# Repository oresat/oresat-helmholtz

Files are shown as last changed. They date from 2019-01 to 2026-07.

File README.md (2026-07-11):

# OreSat Helmholtz Cage



This repo contains design and operating instructions of a Helmholtz Cage, which uses the [Biot Savart Law](https://en.wikipedia.org/wiki/Biot%E2%80%93Savart_law) to get a desired magnetic field inside of an enclosed space using three pairs of perpendicular coils, one pair for each axis. Our fundamental purpose in doing this is to test cubesats' pointing and detumbling capabilities in LEO.

v2.0 is now underway, utilizing less hardware than v1.0. This is excellent news for everyone involved, as less parts means less things that can and will break. We are using a Raspberry Pi Pico to run it, with each set of coils getting their own motor driver, to drive the current, and a INA226 to monitor the current. A full schematic can be found [here](./controller-v2/helmholtz-controller-v2.kicad_sch). A PCB layout is in the works.

# Design Notes

**Status, design, and testing information can be found in the [OreSat Helmholtz Cage Design Notes](https://docs.google.com/document/d/1s9UlxD-V_3-_QfmXqKaY5oYsfC2GDHxeAkWD0VgjS5g/edit?tab=t.0).**

A seperate doc on the structure and design of the cage itself can be found [here](./docs/Open%20Source%20Document.docx). This doc is a bit out of date in some aspects, mainly the technical hardware, but serves as a good resource for cage construction and theory.

## Pictures
MCECS BETA Project 2018:


Current Build:
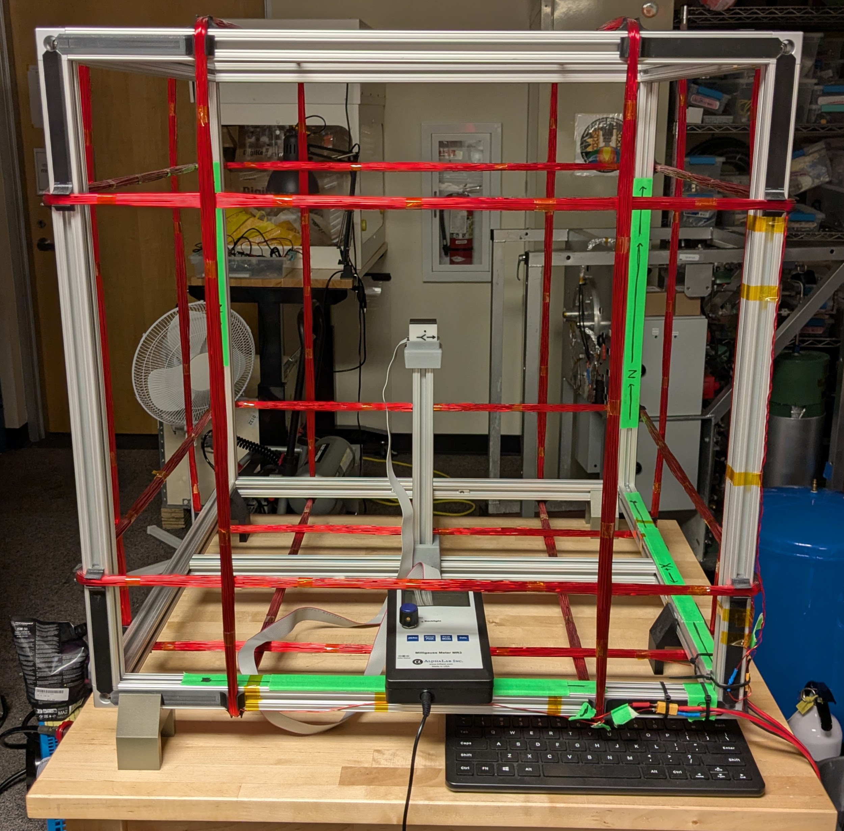
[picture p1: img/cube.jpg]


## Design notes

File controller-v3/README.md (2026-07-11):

---
title: "**Helmholtz Cage Controller v3.0**"
subtitle: |
  **Fabrication and Assembly Information**\
  For build TIME-STAMP
fontsize: 10pt
geometry:
  - margin=0.5in
toc: true
toc-depth: 2
colorlinks: true
urlcolor: blue
---

\newpage

# About this Board

## Board Description

This board controls the magnetic field in a small box with 3 double electromagnetic coils. 

TODO: MOAR

## Documentation Links

- Helmholtz Cage Controller v3: <https://github.com/oresat/oresat-helmholtz>

## Documentation Files

| Filename                        | Notes                                    |
| ------------------------------- | ---------------------------------------- |
| README.pdf                      | This README file                         |
| PROJECT-NAME-outline.dxf        | Board outline (with holes) in DXF format |
| PROJECT-NAME-pcba.step          | 3D model of PCBA (with components)       |
| PROJECT-NAME-render-bot.jpg     | Render of the top of the 3D model        |
| PROJECT-NAME-render-bot.jpg     | Render of the bottom of the 3D model     |
| PROJECT-NAME-schematic.pdf      | PDF of board schematics                  |

## Contact Information

- Website: <https://www.oresat.org/>
- Email: <oresat@pdx.edu>
- Instagram: @pdxaerospace

## Board Renders

Render of the top of the 3D model
Render of the bottom of the 3D model

\newpage

# Printed Circuit Board (PCB) Fabrication Information

## Board Info

- 2 layer board
- Bounding box is TBD
- Board thickness is 1.59 mm (0.063 inch)

## Board Requirements

- Design Rules
    - Minimum Trace / Space design rulea: 0.1524 mm (6.0 mil) / 0.1524 mm (6.0 mil)
    - Outer dimension router tolerance: +/- 0.254 mm (10.0 mil)
    - Hole placement tolerance: +/- 0.075 mm (3.0 mil)
- Drills
   - Drill Positional Tolerance: 0.051 mm (2.0 mil)
   - Drill Size tolerance: +/- 0.064 mm (2.5 mil)
- Plated/Un-plated holes
  - There are no un-plated (NPT) holes
  - There are 96 plated through (PTH) holes
  - PTH minimum diameter: 0.254 mm (10 mil)
  - PTH minimum annulus: 0.102 mm (4 mil) radius
- Outline/Routing
  - No requirements.
- Slots
  - There are no slots.
- Cutouts
  - There are no cutouts
- There are 3 fiducials on the top layer.
- Panel tabs ("mouse bites")
   - Card edges must be smooth; no mouse bites or other intrusions into the card outline.
   - If external mouse bites are required, minimize and customer will remove by hand before assembly.
- If not otherwise specified, build to IPC 6012 Class 2 or better.

## Materials

- No requirements for materials.
- Copper Surface treatment should be ENIG, althogh immersion Silver is acceptable.
- White silkscreen on top and bottom surface
- Taiyo PSR-4000 or equivalent soldermask on top and bottom, no requirements for color.

## Stack Up

- Any FR4 like material is acceptable.
- 1 oz Copper on top and bottom layers
- 1.6 mm thick when done (1/16 inch)

## Array / Panel Information

- Coordinate with Contract Manufacturer (CM) for optimal size of this panel.
- If no feedback from CM, then produce single boards (no panel).

## Fabrication Files

### IPC-2581 File

| Filename                 | Notes                                   |
| ------------------------ | --------------------------------------- |
| PROJECT-NAME-ipc2581.xml | IPC-2581 board information file         |

### Legacy PCB Files

| Filename                      | Notes                                         |
| ------------------------------| --------------------------------------------- |
| PROJECT-NAME-Edge_Cuts.gbr    | RS274X file for the dimension (outline) layer |
| PROJECT-NAME-F_Silkscreen.gbr | RS274X file for the top silkscreen            |
| PROJECT-NAME-F_Mask.gbr       | RS274X file for the top soldermask            |
| PROJECT-NAME-F_Cu.gbr         | RS274X file for the top copper layer          |
| PROJECT-NAME-In1_Cu.gbr       | RS274X file for the layer 2 copper            |
| PROJECT-NAME-In2_Cu.gbr       | RS274X file for the layer 3 copper            |
| PROJECT-NAME-B_Cu.gbr         | RS274X file for the bottom copper layer       |
| PROJECT-NAME-B_Mask.gbr       | RS274X file for the bottom soldermask         |
| PROJECT-NAME-B_Silkscreen.gbr | RS274X file for the bottom silkscreen         |
| PROJECT-NAME-NPTH.drl         | Excellon file for non-plated through holes    |
| PROJECT-NAME-PTH.drl          | Excellon file for plated through holes        | 

\newpage

# Printed Circuit Board Assembly (PCBA) Information

## Assembly Info

- All components are on the top side of the board.

## Assembly Requirements

- Assemble to IPC Class 2 or better
- Solder paste can be ROHS or leaded.
- No clean, or Aqueous flux and wash, can be used.
- No conformal coating.

## Component Specific Assembly Information

- None

## Assembly Files

### IPC-2581 File

| Filename                 | Notes                           |
| ------------------------ | ------------------------------- |
| PROJECT-NAME-ipc2581.xml | IPC-2581 board information file |

### Bill of Materials (BOM)

| Filename             | Description                            |
| -------------------- | -------------------------------------- |
| PROJECT-NAME-bom.csv | BOM in Comma Separated Variable format |

### Solder Paste Stencils

| Filename                 | Notes                                            |
| ------------------------ | ------------------------------------------------ |
| PROJECT-NAME-B_Paste.gbr | RS274X file for top/front solder paste stencil   |
| PROJECT-NAME-F_Paste.gbr | RS274X file for bottom/back solder paste stencil |

### Mounting/Placement Location

| Filename            | Description                                 |
| ------------------- | ------------------------------------------- |
| PROJECT-NAME-3u.pos | Pick and place locations for components     |

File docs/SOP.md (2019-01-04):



# OreSat Helmholtz Cage: Standard Operating Procedure

## General Notes:

* Operate the cage with 4.92 max amps and 15.20 max volts to output the largest magnetic field vector.
* Theoretical magnetic field vector equation:

  * Bz is the total field produced by both square coils as a function of the axial distance z from the center of the coils
  * u0 is the permeability of free space: 4pi*10^-7 WB A^-1 m^-1
  * n is the number of turns of wire: 58 turns
  * I is the current of the wire being analyzed: user input
  * h is the distance between the coils: 
  * a is one half the side length of the structure: 
  
**Do not operate the Helmholtz Cage if the vacuum chamber is on!**

---
## Safety:

* The red coils will get hot if operated for an extended period of time at high currents. Do not touch or hold the coils when operating the cage.
* Monitor the temperature of the wires to maintain a safe operating temperature below 140°C.
* Monitor the temperature of the main power supply to operate between -25°C to 70°C.
* If the temperature begins to approach the operating limits, turn off the power supply and let the cage cool down before resuming testing.

**Do not operate the Helmholtz Cage if the vacuum chamber is on!**

---
## Prepping the Cage:

1. It is safe to put electronic devices inside and around the cage. However, they may disrupt the magnetic field and cause discrepancies in testing data. Be mindful of this and be aware of the testing space surroundings.
2. Verify that the vacuum chamber is NOT on.
3. Verify that the coils are secured in the terminal blocks and make sure they are connected to the correct terminals/power supply. No exposed or crossing wires!
4. Turn on the surge protector. This will power the raspberry pi, monitor, power supplies, and cage.
5. Let the raspberry pi boot up.
6. Turn the keyboard and the mouse on. There are spare batteries in the tote just in case.

---
## Operating the Cage Program:

TBD

---
## Testing & Analyzing Data:

TBD

---
## While the Helmholtz Cage is Running:

* Do not leave the cage unattended. You must monitor it constantly in case of a fire, to maintain safe temperatures for components, and to ensure accurate data collection.
* When the cage is running, do not touch or hold the red coils! They get hot and can cause injury/burns.
* Turn off the surge protector to turn the cage of for any reason.

---
## Finishing Up:

1. Once testing is completed, turn off the raspberry pi using the desktop menu.
2. Wait for the raspberry pi to shutdown completely.
3. Turn off the keyboard and mouse!! Don’t waste the batteries!
4. Flip off the surge protector to power down the power supplies, monitor, and cage.
5. If you adjusted the coil placement, wait until the red wire is cool to the touch before returning the coils to their originally labelled terminals.
6. Clean up after yourself and keep the workstation organized!

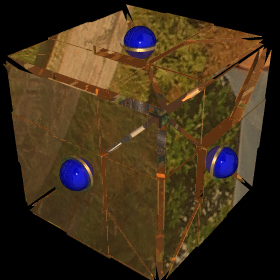
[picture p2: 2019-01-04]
img/holtz.jpg

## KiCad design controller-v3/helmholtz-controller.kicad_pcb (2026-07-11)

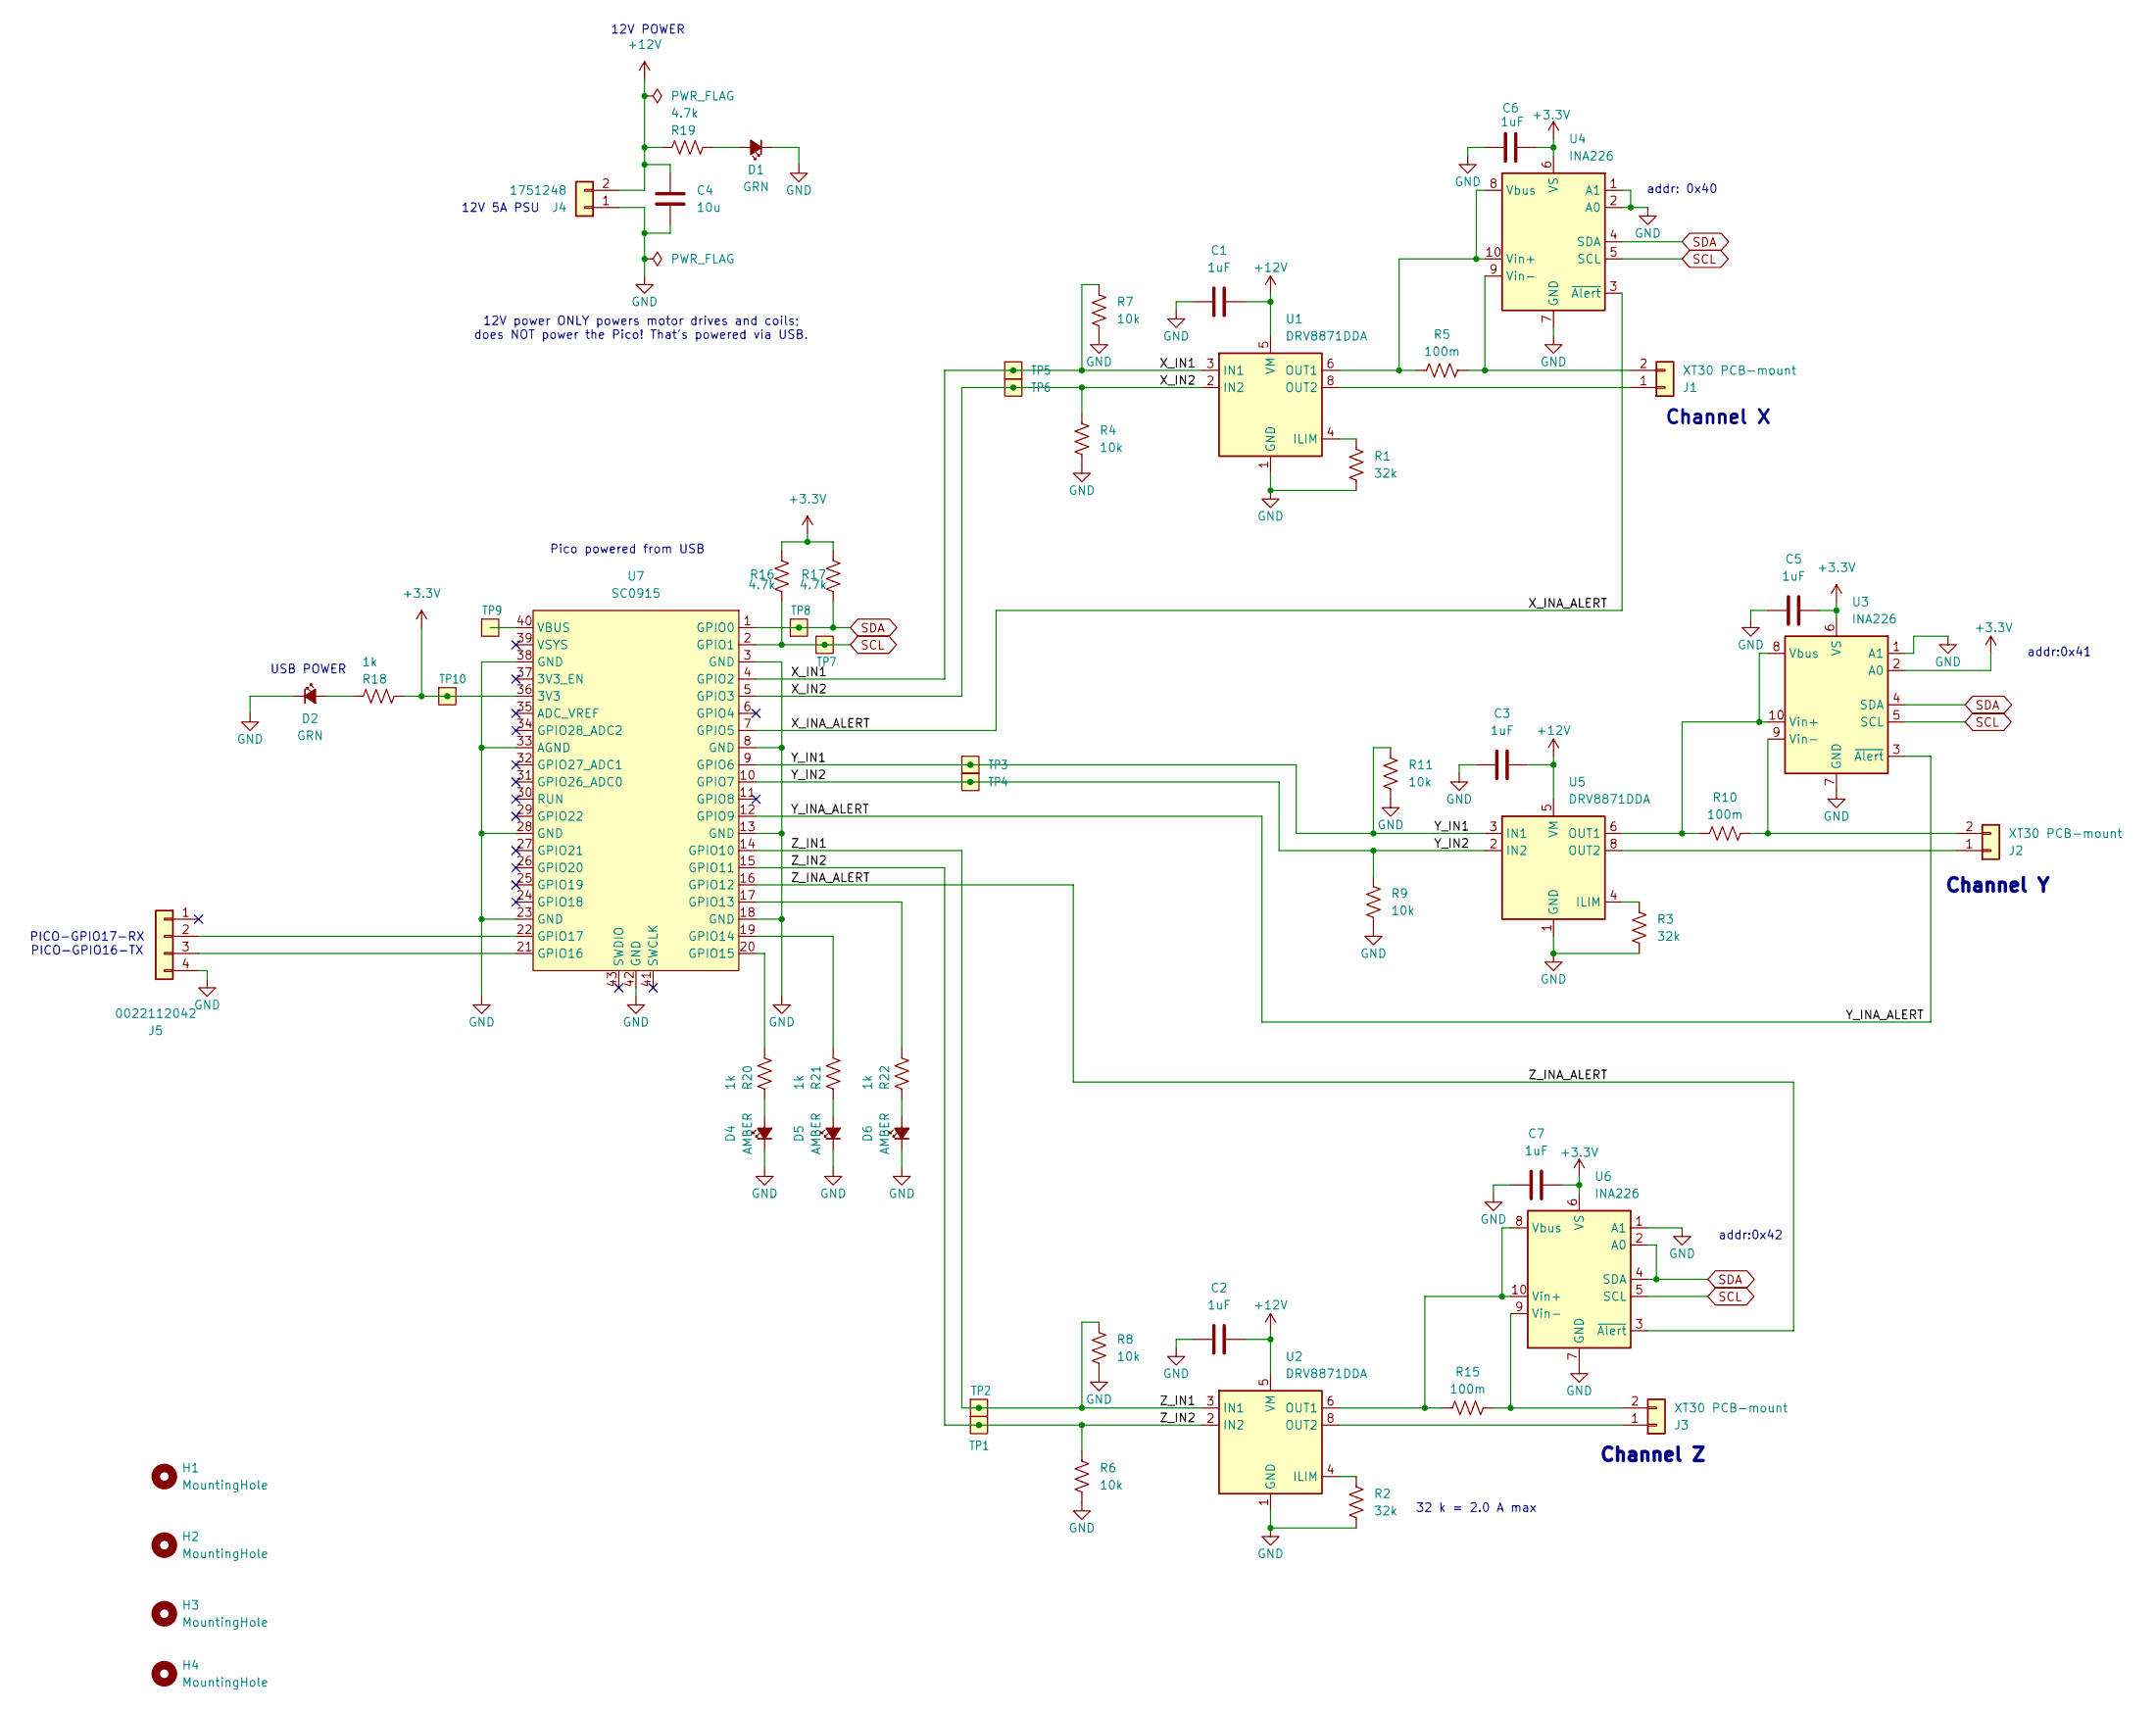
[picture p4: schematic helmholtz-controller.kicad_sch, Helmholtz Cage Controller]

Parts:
C1, C2, C3, C5, C6, C7: 1uF; C_0805_2012Metric; MPN GCM21BR71H105KA03L
C4: 10u; C_0805_2012Metric; MPN GRT21BC71E106KE13K
D1, D2: GRN; LED_0603_1608Metric; MPN 150060GS75000
D4, D5, D6: AMBER; LED_0603_1608Metric; MPN 150060AS75000
H1, H2, H3, H4: MountingHole; MountingHole_3.2mm_M3
J1, J2, J3: XT30 PCB-mount; AMASS_XT30PW-F_1x02_P2.50mm_Horizontal
J4: 1751248; TerminalBlock_Phoenix_PT-1,5-2-3.5-H_1x02_P3.50mm_Horizontal; MPN 1751248
J5: 0022112042; PinHeader_1x04_P2.54mm_Vertical; MPN 0022112042
R1, R2, R3: 32k; R_0603_1608Metric; MPN RNCF0603BTE32K0
R4, R6, R7, R8, R9, R11: 10k; R_0603_1608Metric; MPN RMCF0603FT10K0
R5, R10, R15: 100m; R_1206_3216Metric; MPN CSR1206FTR100
R16, R17, R19: 4.7k; R_0603_1608Metric; MPN RC0603FR-074K7L
R18, R20, R21, R22: 1k; R_0603_1608Metric; MPN RMCF0603FT1K00
TP1, TP2, TP3, TP4, TP5, TP6, TP7, TP8, TP9, TP10: Test-Point; TestPoint-0.75mm-th
U1, U2, U5: DRV8871DDA; Texas_HTSOP-8-1EP_3.9x4.9mm_P1.27mm_EP2.95x4.9mm_Mask2.4x3.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; MPN DRV8871DDA
U3, U4, U6: INA226; TSSOP-10_3x3mm_P0.5mm; MPN INA226AIDGST
U7: SC0915; RPi_Pico_Castellated; MPN SC0915

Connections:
+3.3V: C5.2, C6.2, C7.2, R16.2, R17.2, R18.2, TP10.1 (1_1), U3.2 (A0), U3.6 (VS), U4.6 (VS), U6.6 (VS), U7.36 (3V3)
+12V: C1.2, C2.2, C3.2, C4.2, J4.2, R19.1, U1.5 (VM), U2.5 (VM), U5.5 (VM)
/X_IN1: R7.1, TP5.1 (1_1), U1.3 (IN1), U7.4 (GPIO2)
/X_IN2: R4.1, TP6.1 (1_1), U1.2 (IN2), U7.5 (GPIO3)
/X_INA_ALERT: U4.3 (~Alert), U7.7 (GPIO5)
/Y_IN1: R11.1, TP3.1 (1_1), U5.3 (IN1), U7.9 (GPIO6)
/Y_IN2: R9.1, TP4.1 (1_1), U5.2 (IN2), U7.10 (GPIO7)
/Y_INA_ALERT: U3.3 (~Alert), U7.12 (GPIO9)
/Z_IN1: R8.1, TP2.1 (1_1), U2.3 (IN1), U7.14 (GPIO10)
/Z_IN2: R6.1, TP1.1 (1_1), U2.2 (IN2), U7.15 (GPIO11)
/Z_INA_ALERT: U6.3 (~Alert), U7.16 (GPIO12)
GND: C1.1, C2.1, C3.1, C4.1, C5.1, C6.1, C7.1, D1.1 (K), D2.1 (K), D4.1 (K), D5.1 (K), D6.1 (K), J4.1, J5.4, R1.2, R2.2, R3.2, R4.2, R6.2, R7.2, R8.2, R9.2, R11.2, U1.1 (GND), U1.7 (GND), U1.9 (GND), U2.1 (GND), U2.7 (GND), U2.9 (GND), U3.1 (A1), U3.7 (GND), U4.1 (A1), U4.2 (A0), U4.7 (GND), U5.1 (GND), U5.7 (GND), U5.9 (GND), U6.1 (A1), U6.7 (GND), U7.3 (GND), U7.8 (GND), U7.13 (GND), U7.18 (GND), U7.23 (GND), U7.28 (GND), U7.33 (AGND), U7.38 (GND), U7.42 (GND)
unnamed: D1.2 (A), R19.2
unnamed: D2.2 (A), R18.1
unnamed: D4.2 (A), R20.1
unnamed: D5.2 (A), R21.1
unnamed: D6.2 (A), R22.1
unnamed: J1.1, U1.8 (OUT2)
unnamed: J1.2, R5.2, U4.9 (Vin-)
unnamed: J2.1, U5.8 (OUT2)
unnamed: J2.2, R10.2, U3.9 (Vin-)
unnamed: J3.1, U2.8 (OUT2)
unnamed: J3.2, R15.2, U6.9 (Vin-)
unnamed: J5.2, U7.22 (GPIO17)
unnamed: J5.3, U7.21 (GPIO16)
unnamed: R1.1, U1.4 (ILIM)
unnamed: R5.1, U1.6 (OUT1), U4.8 (Vbus), U4.10 (Vin+)
unnamed: R2.1, U2.4 (ILIM)
unnamed: R15.1, U2.6 (OUT1), U6.8 (Vbus), U6.10 (Vin+)
unnamed: R10.1, U3.8 (Vbus), U3.10 (Vin+), U5.6 (OUT1)
unnamed: R3.1, U5.4 (ILIM)
unnamed: R22.2, U7.17 (GPIO13)
unnamed: R21.2, U7.19 (GPIO14)
unnamed: R20.2, U7.20 (GPIO15)
unnamed: TP9.1 (1_1), U7.40 (VBUS)
SCL: R16.1, TP7.1 (1_1), U3.5 (SCL), U4.5 (SCL), U6.5 (SCL), U7.2 (GPIO1)
SDA: R17.1, TP8.1 (1_1), U3.4 (SDA), U4.4 (SDA), U6.2 (A0), U6.4 (SDA), U7.1 (GPIO0)

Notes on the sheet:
12V power ONLY powers motor drives and coils; does NOT power the Pico! That's powered via USB.
addr:0x41
addr:0x42
12V 5A PSU
12V POWER
addr: 0x40
PICO-GPIO17-RX PICO-GPIO16-TX
Pico powered from USB
USB POWER
Channel Y
Channel Z
Channel X
32 k = 2.0 A max

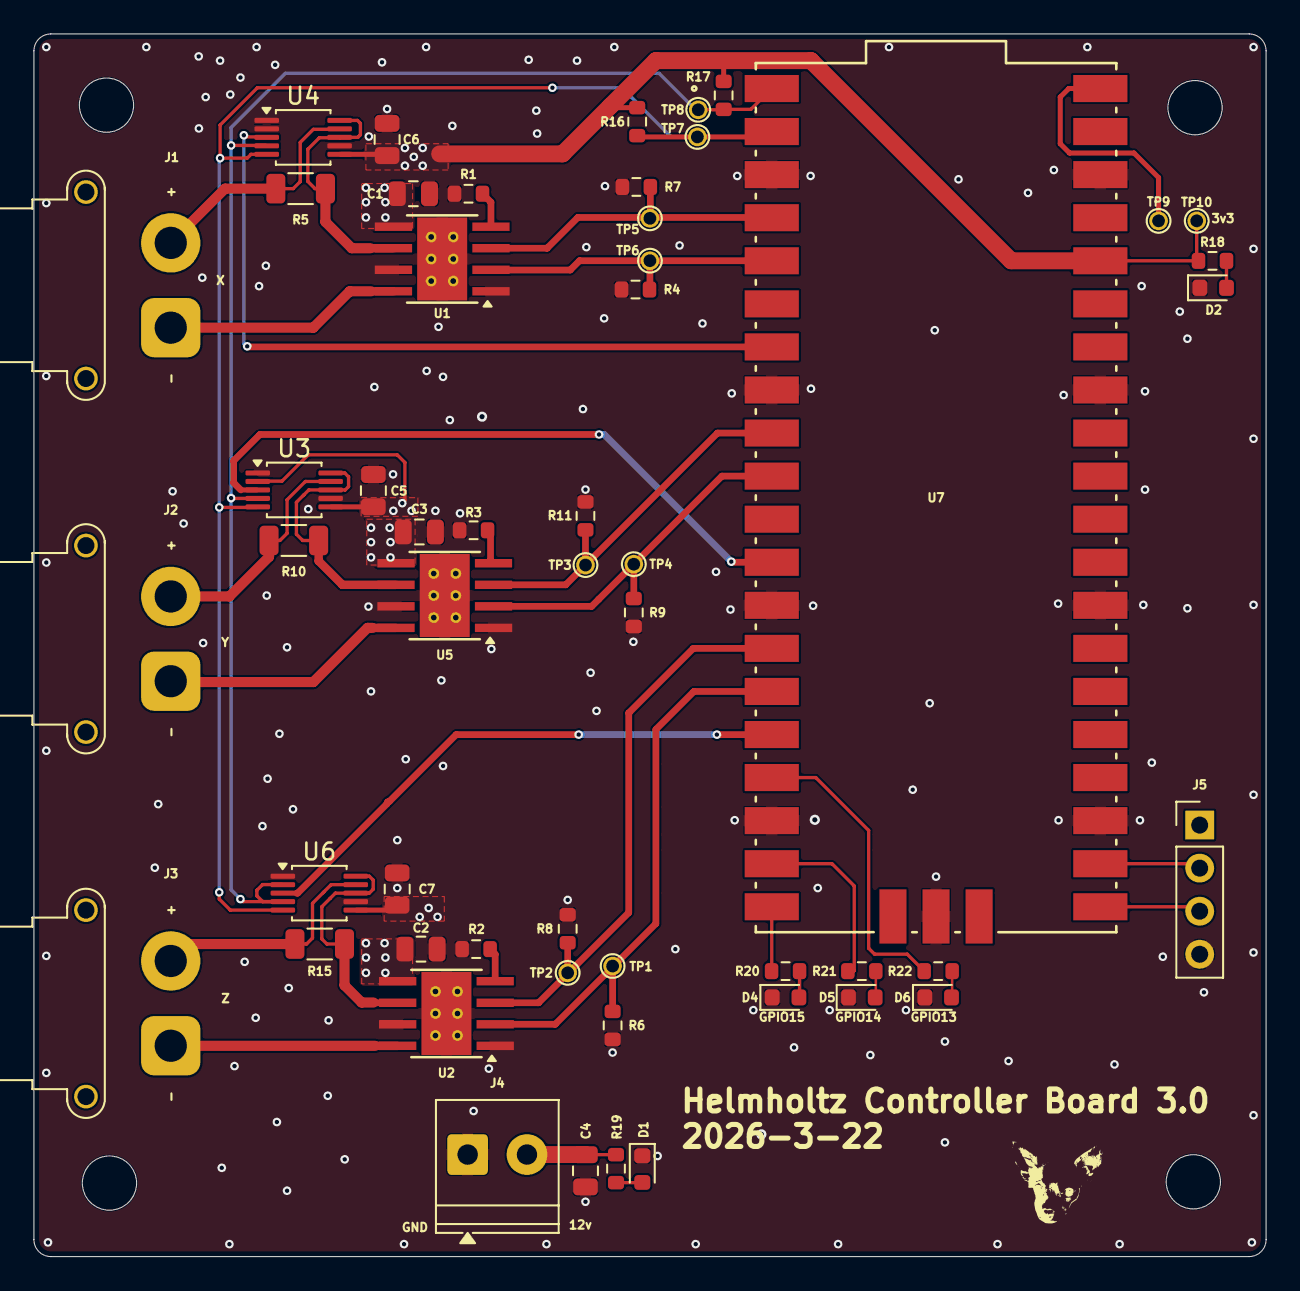
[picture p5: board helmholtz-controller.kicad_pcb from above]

Board: 2 copper layers, 72.7 x 72.1 mm, 57 parts (0 on the bottom side), 37 nets.

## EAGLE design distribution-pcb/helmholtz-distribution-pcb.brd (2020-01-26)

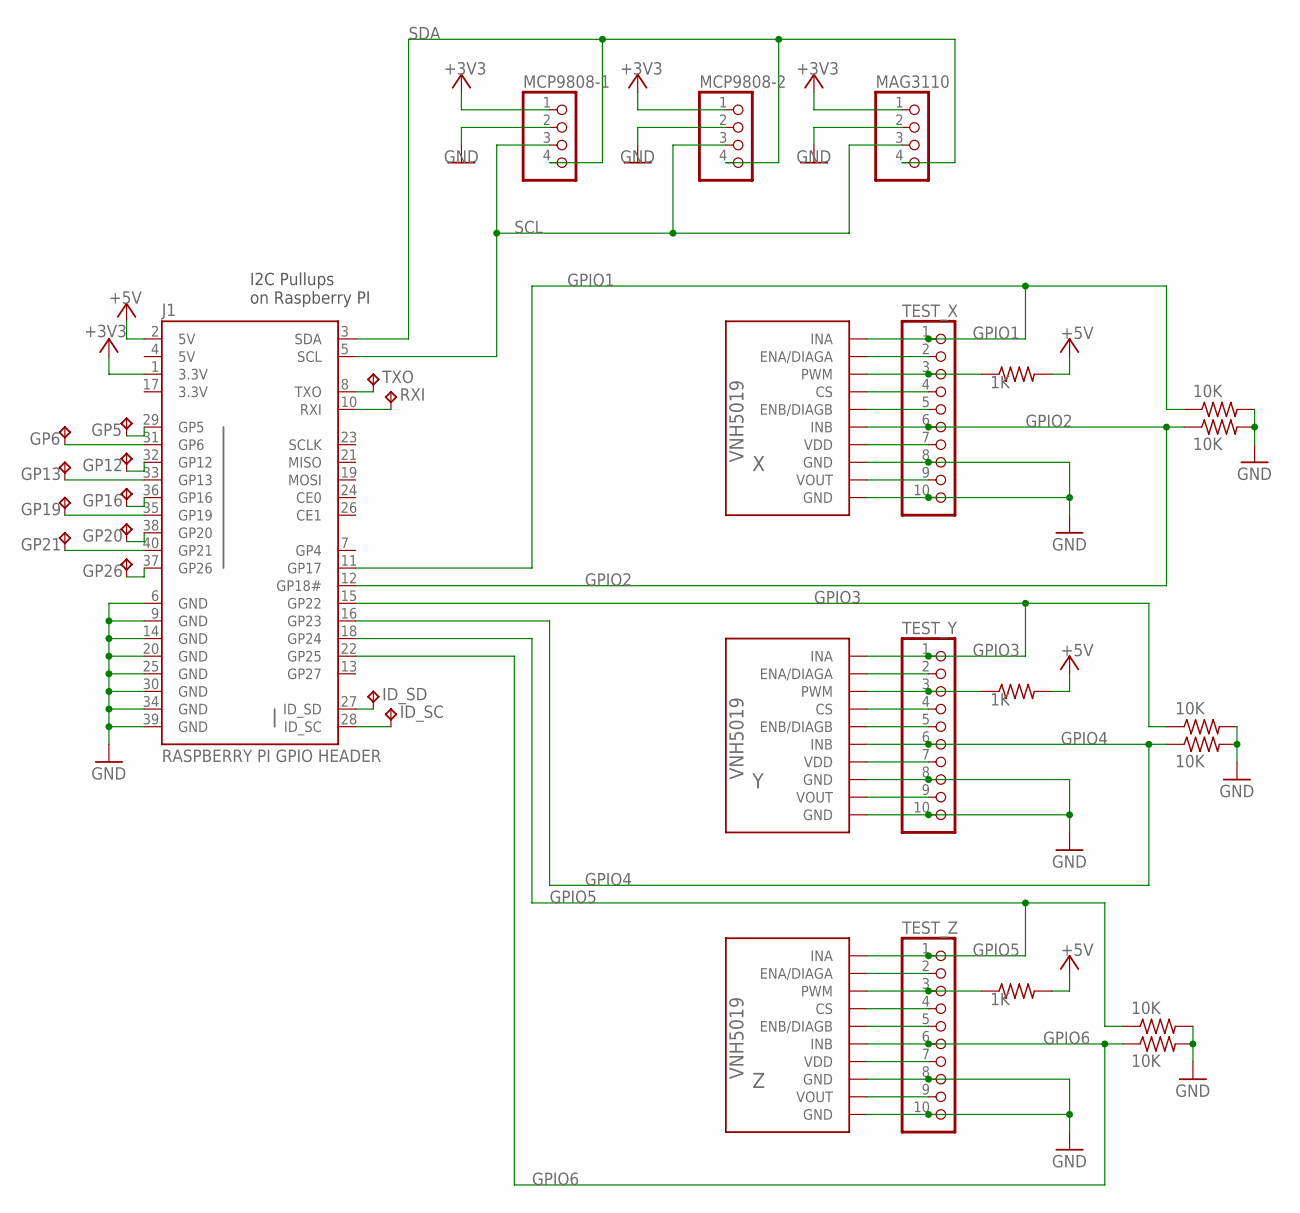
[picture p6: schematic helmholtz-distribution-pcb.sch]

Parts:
GP5, GP6, GP12, GP13, GP16, GP19, GP20, GP21, GP26: TPPAD1-13; P1-13
ID_SC: TPPAD1-13; P1-13
ID_SD: TPPAD1-13; P1-13
J1: RASPBERRYPI-40-PIN-GPIO_PTH; 2X20_SHROUDED
MAG3110: PINHD-1X4; 1X04
MCP9808-1, MCP9808-2: PINHD-1X4; 1X04
R2, R3, R9, R10, R16, R17: 10K; R0603
R7, R13, R20: 1K; R0603
RXI: TPPAD1-13; P1-13
TEST_X: PINHD-1X10; 1X10
TEST_Y: PINHD-1X10; 1X10
TEST_Z: PINHD-1X10; 1X10
TXO: TPPAD1-13; P1-13
X: VNH5019
Y: VNH5019
Z: VNH5019

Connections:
3.3V: J1.17 (3.3V)
5V: J1.4 (5V)
+3V3: J1.1 (3.3V), MAG3110.1, MCP9808-1.1, MCP9808-2.1
+5V: J1.2 (5V), R7.2, R13.2, R20.2
CS_X: TEST_X.4, X.CS
CS_Y: TEST_Y.4, Y.CS
CS_Z: TEST_Z.4, Z.CS
ENA/DIAGA_X: TEST_X.2, X.ENA/DIAGA
ENA/DIAGA_Y: TEST_Y.2, Y.ENA/DIAGA
ENA/DIAGA_Z: TEST_Z.2, Z.ENA/DIAGA
ENB/DIAGB_X: TEST_X.5, X.EBN/DIAGB (ENB/DIAGB)
ENB/DIAGB_Y: TEST_Y.5, Y.EBN/DIAGB (ENB/DIAGB)
ENB/DIAGB_Z: TEST_Z.5, Z.EBN/DIAGB (ENB/DIAGB)
GND: J1.6 (GND), J1.9 (GND), J1.14 (GND), J1.20 (GND), J1.25 (GND), J1.30 (GND), J1.34 (GND), J1.39 (GND), MAG3110.2, MCP9808-1.2, MCP9808-2.2, R2.2, R3.2, R9.2, R10.2, R16.2, R17.2, TEST_X.8, TEST_X.10, TEST_Y.8, TEST_Y.10, TEST_Z.8, TEST_Z.10, X.GND@1 (GND), X.GND@2 (GND), Y.GND@1 (GND), Y.GND@2 (GND), Z.GND@1 (GND), Z.GND@2 (GND)
GPIO1: J1.11 (GP17), R17.1, TEST_X.1, X.INA
GPIO2: J1.12 (GP18#), R16.1, TEST_X.6, X.INB
GPIO3: J1.15 (GP22), R10.1, TEST_Y.1, Y.INA
GPIO4: J1.16 (GP23), R9.1, TEST_Y.6, Y.INB
GPIO5: J1.18 (GP24), R3.1, TEST_Z.1, Z.INA
GPIO6: J1.22 (GP25), R2.1, TEST_Z.6, Z.INB
unnamed: GP26.TP, J1.37 (GP26)
unnamed: GP21.TP, J1.40 (GP21)
unnamed: GP20.TP, J1.38 (GP20)
unnamed: GP19.TP, J1.35 (GP19)
unnamed: GP16.TP, J1.36 (GP16)
unnamed: GP13.TP, J1.33 (GP13)
unnamed: GP12.TP, J1.32 (GP12)
unnamed: GP6.TP, J1.31 (GP6)
unnamed: GP5.TP, J1.29 (GP5)
unnamed: J1.8 (TXO), TXO.TP
unnamed: J1.10 (RXI), RXI.TP
unnamed: ID_SD.TP, J1.27 (ID_SD)
unnamed: ID_SC.TP, J1.28 (ID_SC)
PWM_X: R20.1, TEST_X.3, X.PWM
PWM_Y: R13.1, TEST_Y.3, Y.PWM
PWM_Z: R7.1, TEST_Z.3, Z.PWM
SCL: J1.5 (SCL), MAG3110.3, MCP9808-1.3, MCP9808-2.3
SDA: J1.3 (SDA), MAG3110.4, MCP9808-1.4, MCP9808-2.4
VDD_X: TEST_X.7, X.VDD
VDD_Y: TEST_Y.7, Y.VDD
VDD_Z: TEST_Z.7, Z.VDD
VOUT_X: TEST_X.9, X.VOUT
VOUT_Y: TEST_Y.9, Y.VOUT
VOUT_Z: TEST_Z.9, Z.VOUT

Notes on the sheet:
RASPBERRY PI GPIO HEADER
I2C Pullups on Raspberry PI

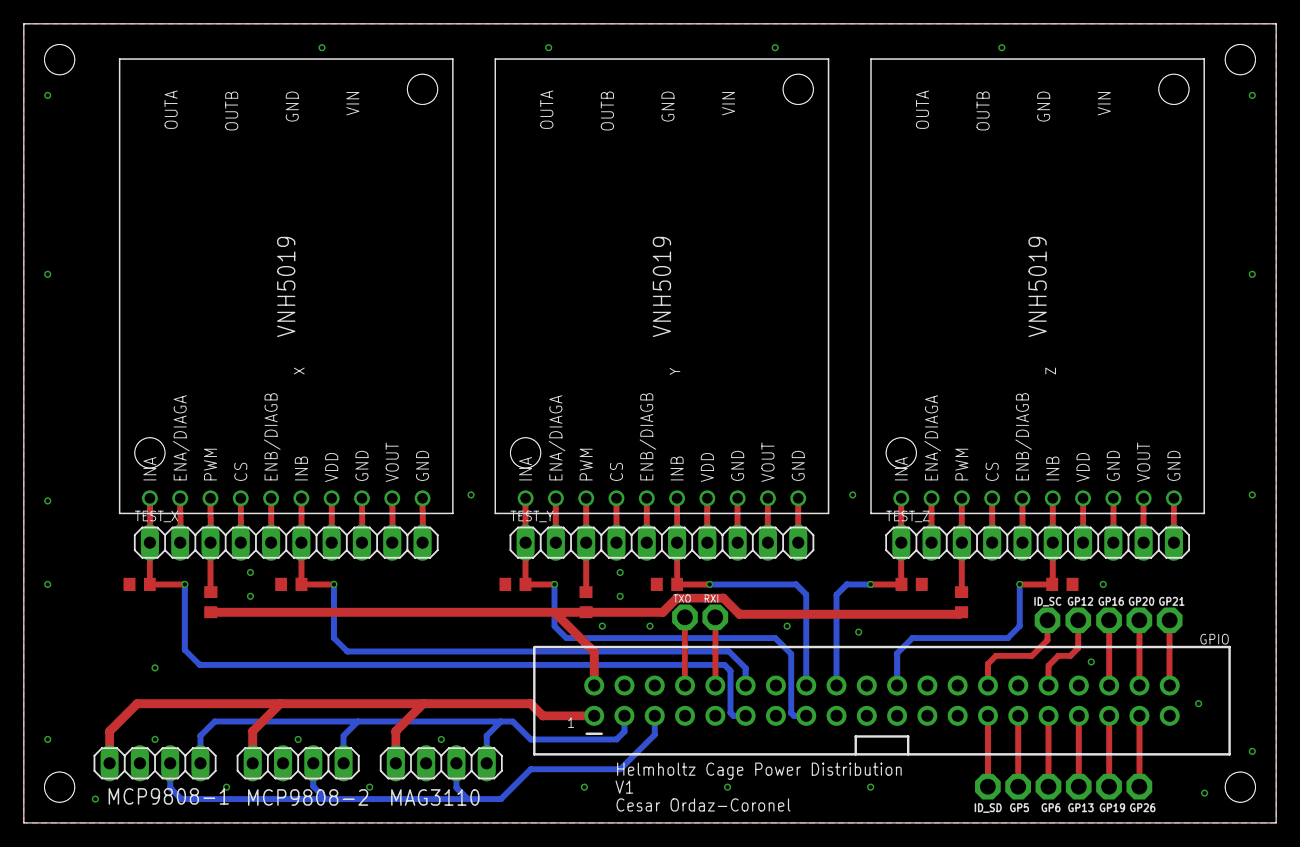
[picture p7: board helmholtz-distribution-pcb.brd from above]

Board: 2 copper layers, 105.0 x 67.0 mm, 32 parts (0 on the bottom side), 42 nets.

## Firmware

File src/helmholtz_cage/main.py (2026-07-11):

import sys
import time

import board
from busio import I2C, UART
from cli import Cli, Command
from data import print_curr_mag_csv, print_dci_csv, print_fields_csv
from ina226 import INA226
from magfield import generate_field, run_calibration_sweep
from motor_driver import MotorDriver, MotorDriverAssembly, set_dc, stop_all_motor_drivers
from uart import print_bridge_vals

import adafruit_logging as logging

LOGGER = logging.getLogger('Helmholtz logger')
LOGGER.setLevel(logging.DEBUG)

LOGGER.info("Oresat Helmholtz Cage Firmware v2")

UART = UART(board.GP16, board.GP17, baudrate=115200, timeout=10, receiver_buffer_size=128)
LOGGER.info("Initialized UART")

I2C = I2C(board.GP1, board.GP0)
LOGGER.info("Initialized I2C bus")

INA226_X = INA226(I2C, 0x40)
INA226_Y = INA226(I2C, 0x41)
INA226_Z = INA226(I2C, 0x42)

MOTOR_X = MotorDriver(in1=board.GP2, in2=board.GP3, led=board.GP13)
MOTOR_Y = MotorDriver(in1=board.GP6, in2=board.GP7, led=board.GP14)
MOTOR_Z = MotorDriver(in1=board.GP10, in2=board.GP11, led=board.GP15)


class CageState:
    def __init__(self):
        # Defaults are derived from previous runs. Don't rely on them.
        self.slopes_and_intercepts = [
            {"name": "x", "slope": 1191, "intercept": -108},
            {"name": "y", "slope": 1134, "intercept": -10},
            {"name": "z", "slope": 984, "intercept": 209},
        ]

    def print_slopes_and_intercepts(self):
        "CLI callback to print the current calibration values"
        s = ""
        for val in self.slopes_and_intercepts:
            s += f"{val['name']} - slope: {val['slope']} intercept: {val['intercept']}\r\n"
        return s


MOTOR_DRIVER_ASSEMBLIES = [
    MotorDriverAssembly(MOTOR_X, INA226_X),
    MotorDriverAssembly(MOTOR_Y, INA226_Y),
    MotorDriverAssembly(MOTOR_Z, INA226_Z),
]
LOGGER.info("Initialized motor driver assemblies")


STATE = CageState()

# run_calibration_sweep(STATE)

LOGGER.info("Initializing CLI")
cli = Cli(prompt="> ")

cli.register_commands(
    [
        Command(
            name="calibrate",
            callback=run_calibration_sweep,
            default_args=[STATE, MOTOR_DRIVER_ASSEMBLIES, UART],
            argspec=None,
            help_text="Run a calibration sweep",
        ),
        Command(
            name="field",
            callback=generate_field,
            default_args=[STATE, MOTOR_DRIVER_ASSEMBLIES],
            argspec=[(("-x",), float), (("-y",), float), (("-z",), float)],
            help_text=(
                "Create the desired field inside the cage.\n"
                "For negative values, wrap the number in quotes."
            ),
        ),
        Command(
            name="dcicsv",
            callback=print_dci_csv,
            default_args=[MOTOR_DRIVER_ASSEMBLIES],
            argspec=[(("-p", "-plane"), str)],
            help_text="Generate a csv of duty cycle to current values",
        ),
        Command(
            name="fieldcsv",
            callback=print_fields_csv,
            default_args=[UART],
            argspec=[(("-t", "-time"), int)],
            help_text="Generate a csv of magfield readings over time (seconds)",
        ),
        Command(
            name="currmagcsv",
            callback=print_curr_mag_csv,
            default_args=[MOTOR_DRIVER_ASSEMBLIES, UART],
            argspec=None,
            help_text="Print a csv of current to magnetic field measurements",
        ),
        Command(
            name="calvals",
            callback=STATE.print_slopes_and_intercepts,
            default_args=None,
            argspec=None,
            help_text="Print the current calibration values",
        ),
        Command(
            name="bridgevals",
            callback=print_bridge_vals,
            default_args=[UART],
            argspec=None,
            help_text="Continuously print the readings from the serial bridge once per second",
        ),
        Command(
            name="setdc",
            callback=set_dc,
            default_args=[MOTOR_DRIVER_ASSEMBLIES],
            argspec=[
                (("-p", "-plane"), str),
                (("-d", "-direction"), str),
                (("-dc", "-dutycycle"), int),
            ],
            help_text="Pwm a motor driver with a duty cycle and read its output current",
        ),
        Command(
            name="stop",
            callback=stop_all_motor_drivers,
            default_args=[MOTOR_DRIVER_ASSEMBLIES],
            argspec=None,
            help_text="Stop all motor drivers",
        ),
    ]
)

ctrl_c_last_seen = -1

while True:
    try:
        should_exit = cli.process_incoming_bytes()
        if should_exit:
            break
    except KeyboardInterrupt:
        if time.monotonic() - ctrl_c_last_seen < 2:
            break
        else:
            sys.stdout.write("\nPress ctrl-c again to exit")
            cli.redraw_prompt()
            ctrl_c_last_seen = time.monotonic()

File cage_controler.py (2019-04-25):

import os
import serial # Stuff for controlling the power supplies
import time # Stuff for regulated delays
import smbus # Stuff for controlling temperature and magnetic sensors
import magnetic_field_current_relation as mfeq # Stuff for calculating the magnetic field
import utilities as utils # Stuff for debugging and/or general info

sensors = []
SENSOR_INPUT_DELAY = 0.2
SENSOR_ADDRS = [ 'ttyUSB0', 'ttyUSB1', 'ttyUSB2' ]

WIRE_WARN_TEMP = 100 # Min cage wire temperatures in F for warning
WIRE_HCF_TEMP = 120 # Max cage wire temperatures in F for forced halting
PSU_WARN_TEMP = 35 # Min cage wire temperatures in F for warning
PSU_HCF_TEMP = 40 # Max cage wire temperatures in F for forced halting

# Sets voltage in volts of specified power supply unit
def set_volts(voltage, psu_num):
    time.sleep(SENSOR_INPUT_DELAY)
    sensors[i].write("Asu" + str(voltage * 100) + "\n")

# Sets current in amps of specified power supply unit
def set_amps(amps, psu_num):
    if(amps < 0):
        amps = 0 - amps
        utils.log(1, "Implicitly inverting the polarity of power supply " + str(psu_num) + ' to fit the input!')

    time.sleep(.1)
    sensors[psu_num].write("Asi" + str(amps * 1000) + "\n")

# Toggles all power supply units to specified mode
def toggle_all_power_supply(mode):
    for i in range(1, 4):
        toggle_single_power_supply(mode, i)

# Toggles specified power supply unit
#   mode:
#       0: off
#       1: on
#   psu_num: power supply unit number [1, 2, 3]
def toggle_single_power_supply(mode, psu_num):
    time.sleep(.1)
    power_supply = i_to_psu(psu_num)
    if(utils.DEBUG): utils.log(2, 'Toggling bus: ' + str(power_supply[psu_num]) + ' to mode: ' + str(mode))
    power_supply[psu_num].write("Aso" + str(mode) + "\n")

# Initializes all serialized sensor busses [Will assume '/dev/' for System IO location]
def initialize_all_bus():
    for i in SENSOR_ADDRS:
        sensors[i] = initialize_single_bus('/dev/' + i)

# Initializes specified serialized sensor bus
def initialize_single_bus(port):
    return serial.Serial(
        port=port,
        baudrate=9600,
        parity=serial.PARITY_NONE,
        stopbits=serial.STOPBITS_ONE,
        bytesize=serial.EIGHTBITS,
        timeout=None)

def close_all_bus():
    for i in sensors:
        i.close()

# Converts from beautiful Celsius to terrible Fahrenheit
def c_to_f(temp_in_c):
    return temp_in_c * 1.8 + 32

# data conversion processes for magnetometer and temperature
def checksize(measurement, maxval, offset):
    if measurement > maxval :
        return measurement - offset
    else:
        return measurement

# function to safety check temperatures
def temperature_check_bounds(temp, warning, shutoff):
    if temp > warning:
        utils.log(1, "Reached minimum warning temperature! Try turning off the cage to let it cool off?")
        if temp > shutoff:
            utils.log(1, "Reached maximum warning temperature! Auto-powering down the cage!")
            toggle_all_power_supply(0)

# function to get magnetic field components from sensors
def magnotometer():
    # Get I2C bus
    bus = smbus.SMBus(1)
    time.sleep(SENSOR_INPUT_DELAY)

    # MAG3110 address, 0x0E(14)
    # Select Control register, 0x10(16)
    #        0x01(01)    Normal mode operation, Active mode
    bus.write_byte_data(0x0E, 0x10, 0x01)
    time.sleep(SENSOR_INPUT_DELAY)
    # MAG3110 address, 0x0E(14)
    # Read data back from 0x01(1), 6 bytes
    # X-Axis MSB, X-Axis LSB, Y-Axis MSB, Y-Axis LSB, Z-Axis MSB, Z-Axis LSB
    data = bus.read_i2c_block_data(0x0E, 0x01, 6)

    # Convert the data
    xMag = data[0] * 256 + data[1]
    xMag = checksize(xMag, 32767, 65536)

    yMag = data[2] * 256 + data[3]
    yMag = checksize(yMag, 32767, 65536)

    zMag = data[4] * 256 + data[5]
    zMag = checksize(zMag, 32767, 65536)

    # divide by 10 to convert bit counts to microteslas
    return xMag/10, yMag/10, zMag/10

# function to get (and check) temperatures from sensors
# Sensors located at i2c addresses 0x18 and 0x1c
# Please update if changed
def temperature():
    # 1st sensor for wire temp
    # Distributed with a free-will license.
    # Use it any way you want, profit or free, provided it fits in the licenses of its associated works.
    # MCP9808
    # This code is designed to work with the MCP9808_I2CS I2C Mini Module available from ControlEverything.com.
    # https://www.controleverything.com/content/Temperature?sku=MCP9808_I2CS#tabs-0-product_tabset-2

    # Get I2C bus
    bus = smbus.SMBus(1)

    # MCP9808 address, 0x18(24)
    # Select configuration register, 0x01(1)
    #        0x0000(00)    Continuous conversion mode, Power-up default
    config = [0x00, 0x00]
    bus.write_i2c_block_data(0x18, 0x01, config)
    # MCP9808 address, 0x18(24)
    # Select resolution rgister, 0x08(8)
    #        0x03(03)    Resolution = +0.0625 / C
    bus.write_byte_data(0x18, 0x08, 0x03)

    time.sleep(0.2)

    # MCP9808 address, 0x18(24)
    # Read data back from 0x05(5), 2 bytes
    # Temp MSB, TEMP LSB
    data = bus.read_i2c_block_data(0x18, 0x05, 2)

    # Convert the data to 13-bits
    ctemp1 = ((data[0] & 0x1F) * 256) + data[1]
    ctemp1 = checksize(ctemp1, 4095, 8192)
    ctemp1 = ctemp1 * 0.0625

    # 2nd sensor for PSU temp
    #------------------------------------
    bus.write_i2c_block_data(0x1c, 0x01, config)
    bus.write_byte_data(0x1c, 0x08, 0x03)

    time.sleep(0.2)

    data = bus.read_i2c_block_data(0x1c, 0x05, 2)

    ctemp2 = ((data[0] & 0x1F) * 256) + data[1]
    ctemp2 = checksize(ctemp2, 4095, 8192)
    ctemp2 = ctemp2 * 0.0625

    # wire: 100 warn-120 danger, psu: 35 warn-40 danger
    temperature_check_bounds(ctemp1, WIRE_WARN_TEMP, WIRE_HCF_TEMP)
    temperature_check_bounds(ctemp2, PSU_WARN_TEMP, PSU_HCF_TEMP)
    return ctemp1, ctemp2

def poll_data(duration = 10.0, dt = 1.0):
    time_step = [0.0]
    # temp_array = [temperature()]
    mag_array = [magnotometer()]
    while time_step[-1] < duration:
        time.sleep(dt)
        time_step.append(time_step[-1] + dt)
        # temp_array.append(temperature())
        mag_array.append(magnotometer())
    return time_step, mag_array #temp_array, mag_array

def print_data():
    time, mag = poll_data(20, 1)
    i = 0
    for t in time:
        print(time[i], mag[i])
        i += 1

def plot_graph(dt = 1.0):
    t = [0.0] # time
    x_var, y_var, z_var = magnotometer() # mag
    x = [x_var]
    y = [y_var]
    z = [z_var]

    plt.ion()
    fig = plt.figure()
    ax = fig.add_subplot(111)
    xline, = ax.plot(t, x, 'r-')
    yline, = ax.plot(t, y, 'g-')
    zline, = ax.plot(t, z, 'b-')

    while True:
        t.append(t[-1] + dt)
        x_var, y_var, z_var = magnotometer() # mag
        x.append(x_var)
        y.append(y_var)
        z.append(z_var)

        xline.set_xdata(t)
        yline.set_xdata(t)
        zline.set_xdata(t)

        xline.set_ydata(x)
        yline.set_ydata(y)
        zline.set_ydata(z)

        plt.gca().relim()
        plt.gca().autoscale_view()
        fig.canvas.draw()
        time.sleep(dt)
        fig.canvas.flush_events()

# function for controlling subfunctions, given their index
def controller(control):
    if control == 0:
        print("\nExiting...")
    elif control == 1:
        v1 = float(input('Enter desired Voltage: '))
        p1 = int(input('Select the power supply: '))
        set_volts(v1, p1)
        log(0, "\nVoltage set to %s on PSU %d." % (v1, p1))
    elif control == 2:
        a1 = float(input('Enter desired Amperage: '))
        p1 = int(input('Select the power supply: '))
        set_amps(a1, p1)
        log(0, "\nAmperage set to %s on PSU %d." % (a1, p1))
    elif control == 3:
        toggle_all_power_supply(1)
        log(0, "Powering On...")
    elif control == 4:
        toggle_all_power_supply(0)
        log(0, "Powering Off...")
    elif control == 5:
        log(0, "Checking temperatures...")
        ctemp1, ctemp2 = temperature()
        # Output data to screen
        print("Sensor 1")
        print("Temperature in Celsius is    : %.2f C") % ctemp1
        print("Temperature in Fahrenheit is : %.2f F") % c_to_f(ctemp1)
        print("Sensor 2")
        print("Temperature in Celsius is    : %.2f C") % ctemp2
        print("Temperature in Fahrenheit is : %.2f F") % c_to_f(ctemp2)
    elif control == 6:
        print("Checking magnotometer, units in microTeslas")
        xMag, yMag, zMag = magnotometer()
        # Output data to screen
        print("Magnetic field in X-Axis : %d") % xMag
        print("Magnetic field in Y-Axis : %d") % yMag
        print("Magnetic field in Z-Axis : %d") % zMag
    elif control == 7:
        #ps3=x, ps2=y, ps1=z
        ps2, ps1, ps3 = mfeq.fieldToCurrent(x0, y0, z0)
        set_amps(ps1, 1)
        set_amps(ps2, 2)
        set_amps(ps3, 3)
        print("\nAmperage set to %s on PSU %d." % (ps1, 1))
        print("\nAmperage set to %s on PSU %d." % (ps2, 2))
        print("\nAmperage set to %s on PSU %d." % (ps3, 3))
    elif control == 8:
        print_data()
    elif control == 9:
        plot_graph()

# function for interacting with the user
def interface():
    control = 1
    while (control != 0):
        print("\nPlease enter a command.")
        print("0 to Exit program \n1 to set Voltage \n2 to set Amperage")
        print("3 to turn On PSU's \n4 to turn Off PSU's")
        print("5 to check temperature sensors \n6 to check magnetic fields")
        print("7 to set a uniform magnetic field\n8 to print some data")
        print("9 to plot a graph\n")

        try:
            control = int(input('Option selected: '))
            controller(control)
        except ValueError:
            print("\n***Invalid Entry***")

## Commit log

2018-11-16 Uploading Bliss's Power Supply Control Code
    Needs updating
2019-02-16 added a little program for getting value of current from magnetic field or vice versa
2019-03-11 cleaning guts. still needs user input but now gives required currents for each power supply based on a desired uniform magnetic field and the measured environmental magnetic fields in each direction
2019-03-22 updated magnetometer function to use microteslas instead of bit counts and fixed warning/danger temperatures for sensors (labelled sensors in comments)
2019-04-17 plotting working somewhat, need to fix axes still, need to fix automatic current setter (check math first)
2019-04-25 Power Bus Init patch
2019-05-02 added a button to close on the main board
2019-10-30 Added Cesar's first version of the distributution board.
    [helmholtz_cage_pcb_design.brd, helmholtz_cage_pcb_design.sch]
2020-01-26 Latest distribution PCB design by Ceasar.
    [helmholtz-distribution-pcb.brd, helmholtz-distribution-pcb.sch, helmholtz_cage_pcb_design.brd]
2020-01-26 Added mounting holes to VNH boards, put mounting holes on board, and changed font to vector.
    [helmholtz-distribution-pcb.brd, helmholtz-distribution-pcb.sch]
2023-02-12 Fast Forward.... 4 years later... (#13)
    * hopefully more accurate
    * some spellchecking and cleaning, also fixing CLI
    * fixed whitespace
    * testing new functionality for motor drivers and automatic current setting
    * squashing bugs
    * bug fixin
    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
2023-05-15 ZXY6005s powersupply library prototype
2023-06-21 Arduino driver WIP
2023-06-23 Arduino Driver WIP v2
2023-06-23 Arduino Driver WIP v2.3
2023-06-26 Arduino driver v2.4
2023-06-29 Updated Arduino Nano code.
2023-08-11 Corrections made to Arduino functions.
2023-08-11 Updated Arduino driver v2.5
2023-08-14 Updated Arduino object constructor and main constructor.
2023-08-14 Updated main to work with updated Arduino driver. Removed properties and made them functions.
2023-08-14 Updated psu power function in main.
2023-08-16 Fixed an issue with ZXY6005s return voltage function.
2023-08-21 Attempt to fix setting the current function in the HC shell.
2023-09-04 Added Calibration Function. Can write to a .CSV and sweep test all axis.
    [sweepdata.csv]
2023-09-14 Added Calibration function help message. WIP
    [sweepdata.csv]
2023-09-14 Fixed calibration parameters
2023-09-14 Fixed an issue where currents were not recorded
2025-02-19 Began designing V2 controller circuit for the Helmholtz Cage
    [Oresat_Helmholtz_Driver.kicad_pcb, Oresat_Helmholtz_Driver.kicad_sch]
2025-03-05 Created schematic for new Helmholtz Cage power driver
    [Oresat Helmholtz Driver.kicad_pcb, Oresat Helmholtz Driver.kicad_sch]
2025-03-12 Added Helmholts Controller V2 with schematic
    [Oresat_Helmholtz_V2.kicad_pcb, Oresat_Helmholtz_V2.kicad_sch]
2025-03-12 Renamed paths for the new controller to be more oresat-y
    [helmholtz-controller-v2.kicad_pcb, helmholtz-controller-v2.kicad_sch]
2025-03-12 Improved schematic, made it more readable
    [helmholtz-controller-v2.kicad_sch]
2025-04-23 ADded 12V connector and I2C resistors
    [helmholtz-controller-v2.kicad_sch]
2025-07-13 Updated README with more current info on v2. Most of that info is in a new doc on the drive, which the README links to.
2025-08-15 updated schematic
    [helmholtz-controller-v2.kicad_pcb, helmholtz-controller-v2.kicad_sch]
2025-08-19 Updated schematic & board
    [helmholtz-controller-v2.kicad_pcb, helmholtz-controller-v2.kicad_sch]
2025-08-22 Indicators & test points added
    [helmholtz-controller-v2.kicad_pcb, helmholtz-controller-v2.kicad_sch]
2025-08-25 Pre-final review
    UART still needs to be connected
    [helmholtz-controller-v2.kicad_pcb, helmholtz-controller-v2.kicad_sch]
2025-08-26 Pre-final Review
    [helmholtz-controller-v2.kicad_pcb, helmholtz-controller-v2.kicad_sch]
2025-08-27 Final Review Ready
    [helmholtz-controller-v2.kicad_pcb]
2025-08-27 Fix BD IC symbols, fix some ERCs, put mounting holes in the schematic.
    [helmholtz-controller-v2.kicad_pcb, helmholtz-controller-v2.kicad_sch]
2025-09-13 Alert pins connected to pico
    [helmholtz-controller-v2.kicad_pcb, helmholtz-controller-v2.kicad_sch]
2025-09-14 Added mounting holes to schematic & connected alert pins on PCB.
    [helmholtz-controller-v2.kicad_pcb, helmholtz-controller-v2.kicad_sch]
2025-10-19 fix schematic and layout sync issues. Begin reworking layout to reduce side flipping.
    [helmholtz-controller-v2.kicad_pcb, helmholtz-controller-v2.kicad_sch]
2025-10-19 Rerouted 3.3v & 12v, added zones
    [helmholtz-controller-v2.kicad_pcb]
2025-10-20 Added zones to shunt resistors
    [helmholtz-controller-v2.kicad_pcb]
2025-10-20 Filled out BOM
    [helmholtz-controller-v2.kicad_sch]
2025-11-22 Final cleanup of board before fab.
    Did some polishing on layout for better power flow.
    [helmholtz-controller-v2.kicad_pcb, helmholtz-controller-v2.kicad_sch]
2025-12-19 Minor changes that bring the version to 2.1.
    The 2.0 board is fabbed, and we found a few minor issues (wrong address listed in the schematic, no XYZ marking at pheonix connectors, etc).
    [helmholtz-controller-v2.kicad_pcb, helmholtz-controller-v2.kicad_sch]
2026-01-07 Fix errors in INA226 driver
    There was a redefinition of a function that looks unfinished, so I
    removed them both. I assume they were supposed to set calibration
    registers with custom values, but at the moment the purpose of the
    functions were unclear because they were unutilized.
2026-01-08 Create flash script
    Without using circuitpython's recommended Mu editor it's kind of a pain
    to flash. Thus I wrote a bash script to ease the process. This will
    probably need to be a little more robust than this to work across
    everyones computers, but this is at least a start for now.
2026-01-08 Delete micropython files
    These were written for micropython, but we're using circuit python, so
    they won't work anymore
2026-01-12 Expand the blink module to work on any led
    Because there are four leds on the board, this will keep things DRY
2026-01-13 Create Motor class
    To help with controlling the motor drivers I've created a motor class
    and associated methods to put it into various modes. I've also assigned
    each motor an led so we can get some visual feedback as to which motor
    is driving (I am assuming that's what the 3 extra leds are for, but this
    could be changed if I'm wrong). It would be nice to be able to tell
    whether or not the motor is driving forward or reverse, but I can't
    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
2026-01-13 Change motor pins from digital to pwm
2026-01-15 Create MR3 communication bridge sub-project
    This will go on the rpi5 and handle streaming/parsing the data from the
    milligauss meter
2026-01-20 rename milligaus_meter to mr3_reader
    semantics
2026-01-20 Switch to struct packing from json, fix mr3 reading errors
    Struct works much better, as it packs straight to bytes, no need to
    encode. The mr3 likes to be asked for data at a rate of 2hz, so sleeping
    for half a second lets the data flow much more cleanly and reliably
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2026-03-13 Started V3. Schematic mostly finished.
    [helmholtz-controller-v2.kicad_pcb, helmholtz-controller-v2.kicad_sch]
2026-03-13 Update to schematic
    [helmholtz-controller-v2.kicad_sch]
2026-03-21 Board mostly laid out
    [helmholtz-controller-v2.kicad_pcb, helmholtz-controller-v2.kicad_sch]
2026-03-22 getting closer to perfect
    [helmholtz-controller-v2.kicad_pcb]
2026-03-22 Minor cleanup on DRC
    [helmholtz-controller-v2.kicad_pcb]
2026-03-26 Some polish
    [helmholtz-controller-v2.kicad_pcb, helmholtz-controller-v2.kicad_sch]
2026-03-26 Requested changes
    [helmholtz-controller-v2.kicad_pcb, helmholtz-controller-v2.kicad_sch]
2026-03-30 Latest push
    [helmholtz-controller-v2.kicad_pcb]
2026-04-23 Helholtz cage controller v3.0, upgrade to KICad 10, new gitignore file
    [helmholtz-controller.kicad_pcb, helmholtz-controller.kicad_sch]
2026-05-25 Fix INA226 configuration
    the ina226 comes preconfigured to expect a maximum of 3.2A, but we limit
    the motor drivers to 2A, so we can configure it to expect that. Also,
    RSHUNT was at 10m ohms, which is wrong, its 100m Ohms, so we were
    getting garbage readings.
2026-05-29 Use slow decay mode
    Using slow decay mode fixes the issue with current collapsing ~50% duty
    cycle. This is achieved by pwm-ing the input that would normally be zero
    according to the truth table while keeping the input that would normally
    be high according to the truth table high. This also means we have to do
    a little math on args to the methods ie subtract the desired duty cycle
    from 100.
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

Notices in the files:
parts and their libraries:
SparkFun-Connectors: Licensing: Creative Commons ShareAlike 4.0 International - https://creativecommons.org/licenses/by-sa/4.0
